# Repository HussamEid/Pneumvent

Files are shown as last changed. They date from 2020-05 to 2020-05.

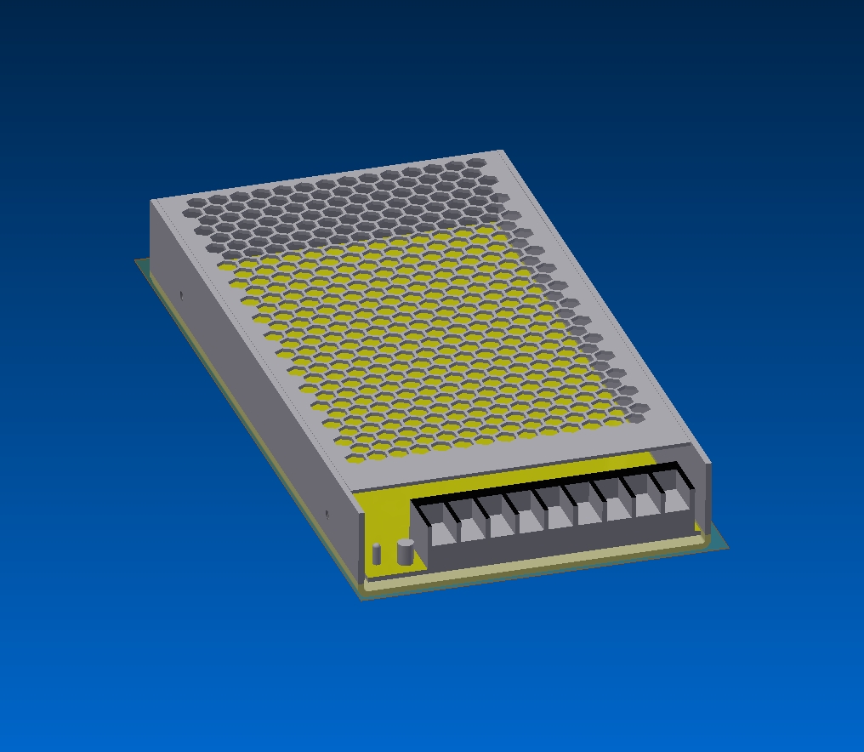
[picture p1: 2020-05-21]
Assembly/LRS-200/Fuente meanwell LRS-200-12.jpg

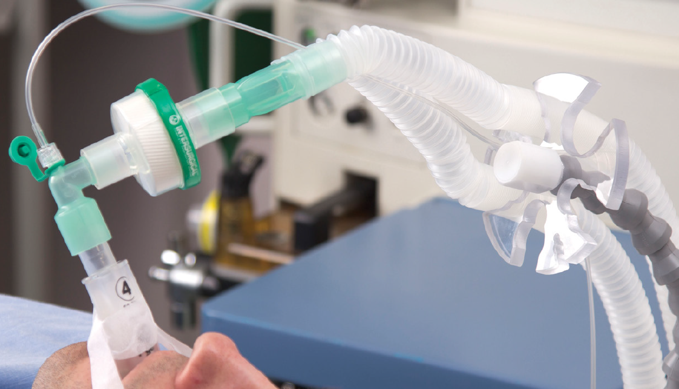
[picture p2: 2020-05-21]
Assembly/Tubing/Overview.PNG

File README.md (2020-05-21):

# Pneumvent
  An open source ICU grade ventilator with feedback control, various operation modes and an easy to use UI. This ventilator was created in response to the COVID-19 pandemic and help address the shortages of the ventilators world wide.
=======
  An open source ICU grade ventilator with feedback control, various operation modes and an easy to use UI. This ventilator was created in response to the COVID-19 pandemic and help address the shortages of the ventilators world wide.
T
>>>>>>> 2d3a161cecc6a0071c0be55cc0cbad3aadb7b60b

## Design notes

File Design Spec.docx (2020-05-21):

# Block Diagram

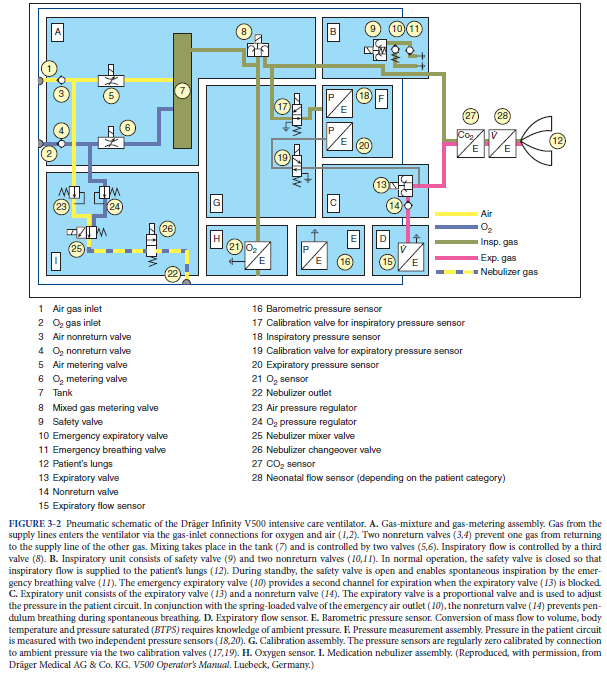
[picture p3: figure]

P.67 (Martin)

# Power Input

INPUT: 110/240VAC @ 50/60Hz,

Battery: 10 – 30VDC

Outlet Pressure (o2/Air): 50psi

Internal Pressure regulator: ~20psi

# Air Conditioning:

Warmed air

Humidified Air

# Mechanism:

Air Compressor or Air blower

# Design Spec

## Battery

The battery requirements are as follows:

12V, at least, 60Ah , lead-acid for reduced cost. This would mean that the system is capable of running at least for 190 mins at full load (worst case scenario).

The battery is connected to the circuit via a screw terminal. The circuit is protected from accidental reverse polarity connection of the battery as well as battery transients due to load variation.

## Power Supply

A three terminal IEC complaint medical grade power entry receptable is used to power the system in case the battery is not used or can be used to charge the battery and power the system if the battery is hooked up the system.

The device can accept voltage inputs ranging from 85VAC to 250VAC and thus can be used around the globe without concern to the outlet voltage.

The system is also fused incase of failure both due to internal and/or external factors. Once the wall power enters the system the whole unit is powered using an Isolated 12V. This means that all users and patients are completely isolated from the mains power supply aacccording ISO 80601.

# Processor

There are multiple sensors (instrumentation) and transducers being monitored and regulated as such a high performance MCU was chosen , in this case STM32F40LVCT6. The MCU will be responsible for :

- Assisting, monitoring and controlling of ventilation
- Control air mixture percentage
- A Human interface beduim to allow the opreator to monitor and control main parameters such as repiratino pressure provide feedback to the users such as control mode and measured snensor data
- Use PID control system algorithm to function 4 valves

The reason this processor was chosen was due to the following:

- High efficency with low voltage (3.3V)
- 32-bit ARM cortex –M4
- 246KB flash memory/512bytes OTP memory /64KB SRAM
- BOR monitoring
- 16 channel ADC (12-bit)
- 11 timers
- 3x I2C interfances
- Accurate measurements and fast control

# Alarm system

Using measured patient data such as exhaled volume and airway pressure, the ventilation system will be able to detect whether a breath has been taken. If the controller detects that no inhalation takes place within a certain period of time the controller will sound a buzzer at 4KHz and 90dB. There are different beeping sequence for different conditions which will be controlled by the MCU.

Also a bright red LED will be flashing to indicate a fault condition.

## Actuators

There are 4 electromechanical valves that are used as following:

- Control O2 input
- Control Air compressor input
- Manage Inhaled air pressure
- Manage Exhaled air pressure

. Each of those valves operate at 5V. Due to the large inductances associated with switching the valves the 5V is galvanically isolated from the MCU and is controlled using optocouplers.

## Pressure Sensors

There are 4 pressure sensors that are used as analog sensor inputs to the MCU to regulate air flow, namey:

1- 1x Lung Pressure Sensor- It is used to calculated the volume of air in the lungs via the pneumotachometer tubing
2- 1x Tank Pressure Sensor- It is used to determine the air to oxygen mixture ratio
3- 2x Differential Pressure Sensor (Flow sensor) used to determine the volume of air inhaled and volume of air exhaled respectively

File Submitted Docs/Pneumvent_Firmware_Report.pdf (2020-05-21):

## Firmware Project Configuration Report

# 1. Description

## 1.1. MCU

MCU Series | STM32F4
MCU Line | STM32F401
MCU name | STM32F401VCTx
MCU Package | LQFP100
MCU Pin number | 100

# PNEUMVENT FIRMWARE REPORT

Agorize- Code Life Ventilator | Hussam Eid | info@hussameid.com

# 2. Pinout Configuration

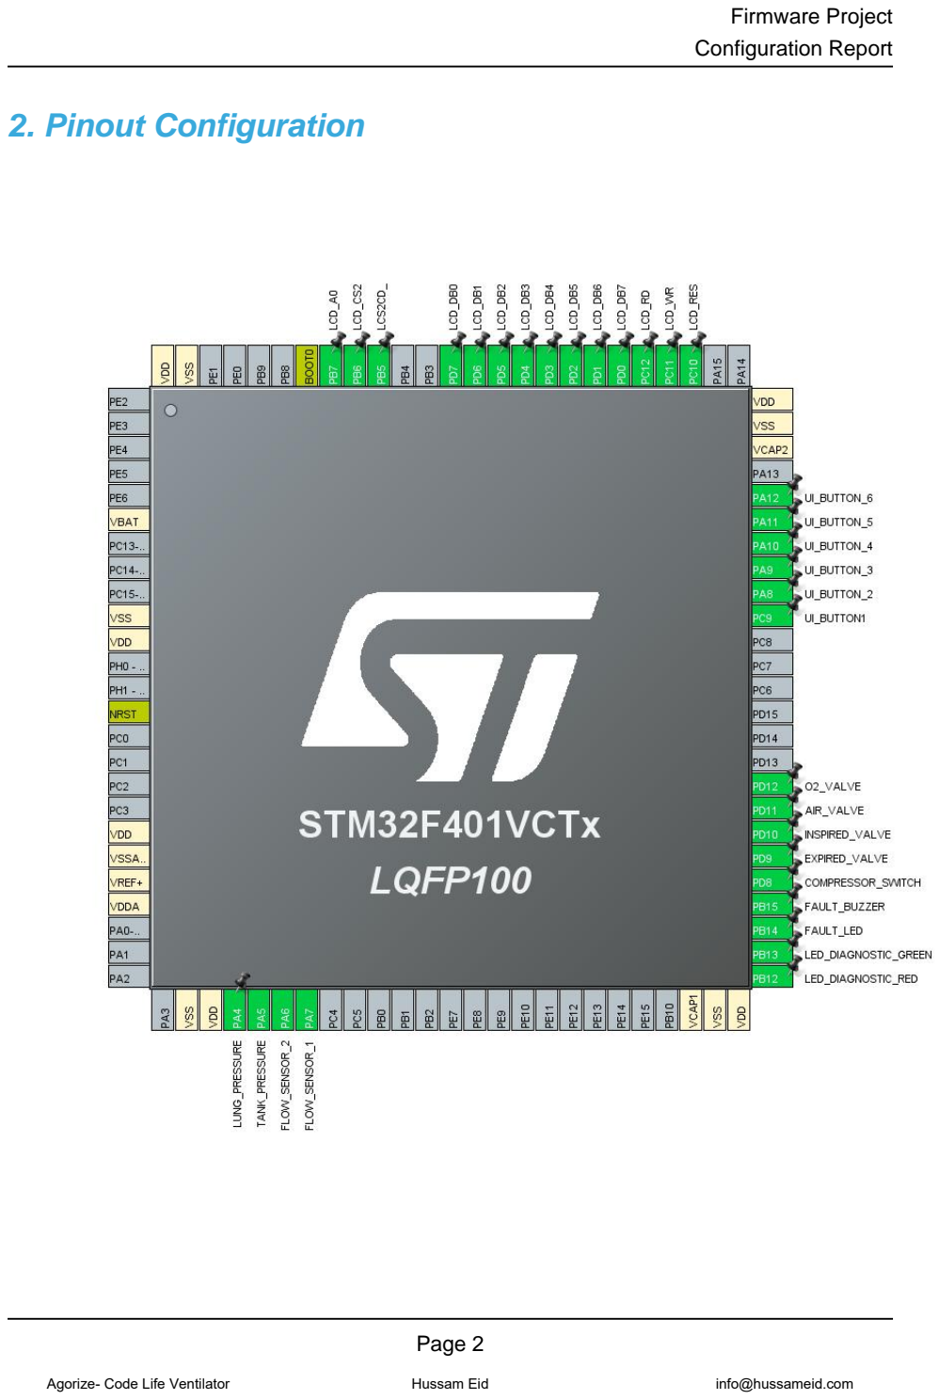
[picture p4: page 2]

# 3. Pins Configuration

Pin Number LQFP100 | Pin Name (function after reset) | Pin Type | Alternate Function(s) | Label
6 | VBAT | Power
10 | VSS | Power
11 | VDD | Power
14 | NRST | Reset
19 | VDD | Power
20 | VSSA/VREF- | Power
21 | VREF+ | Power
22 | VDDA | Power
27 | VSS | Power
28 | VDD | Power
29 | PA4 | I/O | ADC1_IN4 | LUNG_PRESSURE
30 | PA5 | I/O | ADC1_IN5 | TANK_PRESSURE
31 | PA6 | I/O | ADC1_IN6 | FLOW_SENSOR_2
32 | PA7 | I/O | ADC1_IN7 | FLOW_SENSOR_1
48 | VCAP1 | Power
49 | VSS | Power
50 | VDD | Power
51 | PB12 * | I/O | GPIO_Output | LED_DIAGNOSTIC_RED
52 | PB13 * | I/O | GPIO_Output | LED_DIAGNOSTIC_GREE N
53 | PB14 * | I/O | GPIO_Output | FAULT_LED
54 | PB15 * | I/O | GPIO_Output | FAULT_BUZZER
55 | PD8 * | I/O | GPIO_Output | COMPRESSOR_SWITCH
56 | PD9 * | I/O | GPIO_Output | EXPIRED_VALVE
57 | PD10 * | I/O | GPIO_Output | INSPIRED_VALVE
58 | PD11 * | I/O | GPIO_Output | AIR_VALVE
59 | PD12 * | I/O | GPIO_Output | O2_VALVE
66 | PC9 * | I/O | GPIO_Input | UI_BUTTON1
67 | PA8 * | I/O | GPIO_Input | UI_BUTTON_2
68 | PA9 * | I/O | GPIO_Input | UI_BUTTON_3
69 | PA10 * | I/O | GPIO_Input | UI_BUTTON_4
70 | PA11 * | I/O | GPIO_Input | UI_BUTTON_5
71 | PA12 * | I/O | GPIO_Input | UI_BUTTON_6
73 | VCAP2 | Power
74 | VSS | Power
75 | VDD | Power

Pin Number LQFP100 | Pin Name (function after reset) | Pin Type | Alternate Function(s) | Label
78 | PC10 * | I/O | GPIO_Output | LCD_RES
79 | PC11 * | I/O | GPIO_Output | LCD_WR
80 | PC12 * | I/O | GPIO_Output | LCD_RD
81 | PD0 * | I/O | GPIO_Output | LCD_DB7
82 | PD1 * | I/O | GPIO_Output | LCD_DB6
83 | PD2 * | I/O | GPIO_Output | LCD_DB5
84 | PD3 * | I/O | GPIO_Output | LCD_DB4
85 | PD4 * | I/O | GPIO_Output | LCD_DB3
86 | PD5 * | I/O | GPIO_Output | LCD_DB2
87 | PD6 * | I/O | GPIO_Output | LCD_DB1
88 | PD7 * | I/O | GPIO_Output | LCD_DB0
91 | PB5 * | I/O | GPIO_Output | LCS2CD_
92 | PB6 * | I/O | GPIO_Output | LCD_CS2
93 | PB7 * | I/O | GPIO_Output | LCD_A0
94 | BOOT0 | Boot
99 | VSS | Power
100 | VDD | Power

## * The pin is affected with an I/O function

# 4. Clock Tree Configuration

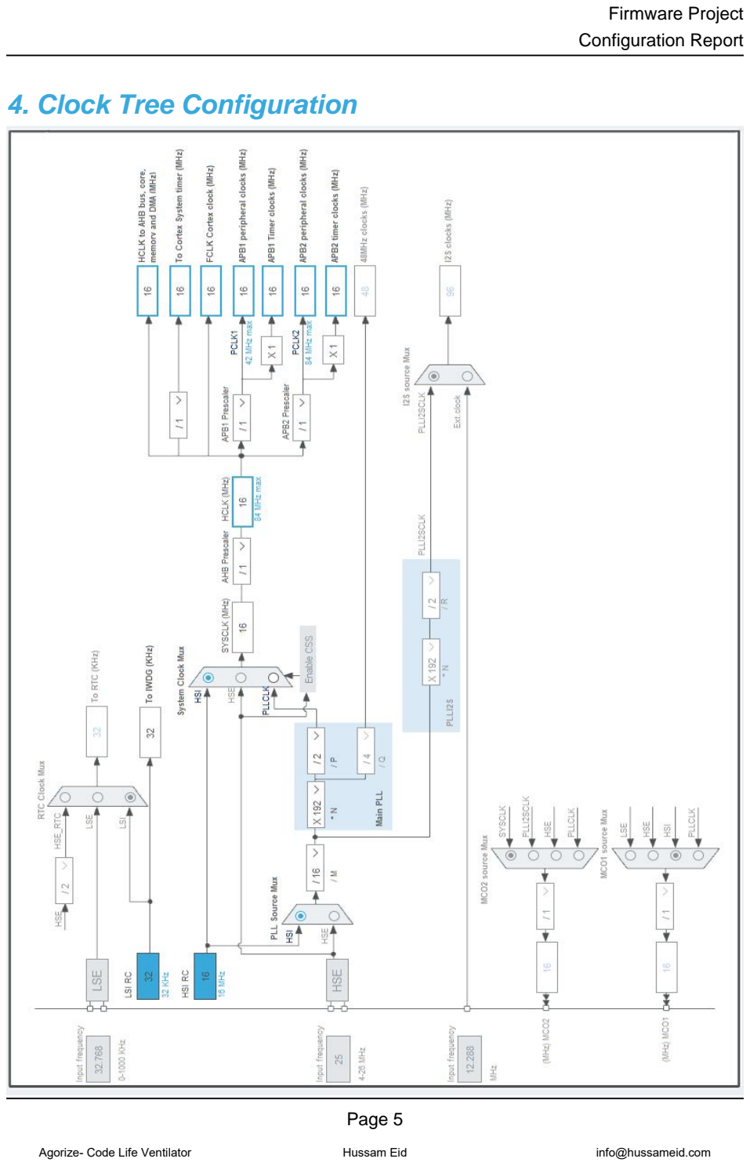
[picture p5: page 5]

# 5. Software Project

## 5.1. Project Settings

# 6. Power Consumption Calculator report

### 6.1. Microcontroller Selection

Series | STM32F4
Line | STM32F401
MCU | STM32F401VCTx
Datasheet | 024738_Rev8

### 6.2. Parameter Selection

Temperature | 25
Vdd | 3.3

### 6.3. Battery Selection

## Battery Capacity Self Discharge

Nominal Voltage | 3.6 V
Max Cont Current | 100.0 mA
Max Pulse Current | 200.0 mA
Cells in series | 1
Cells in parallel | 1

## 6.4. Sequence

Step | Step1 | Step2
Mode | RUN | STOP
Vdd | 3.3 | 3.3
Voltage Source | Battery | Battery
Range | Scale2-Medium | No Scale
Fetch Type | FLASH/ART/PREFETCH | n/a
CPU Frequency | 84 MHz | 0 Hz
Clock Configuration | HSE PLL | Regulator_LPLV Flash-PwrDwn
Clock Source Frequency | 4 MHz | 0 Hz

### Peripherals

Additional Cons. | 0 mA | 0 mA
Average Current | 21.2 mA | 10 µA
Duration | 0.1 ms | 0.9 ms
DMIPS | 105.0 | 0.0
Ta Max | 102.06 | 105
Category | In DS Table | In DS Table

## 6.5. RESULTS

Sequence Time | 1 ms | Average Current | 2.13 mA
Battery Life | 2 months, 5 days, 14 hours | Average DMIPS | 105.0 DMIPS

## 6.6. Chart

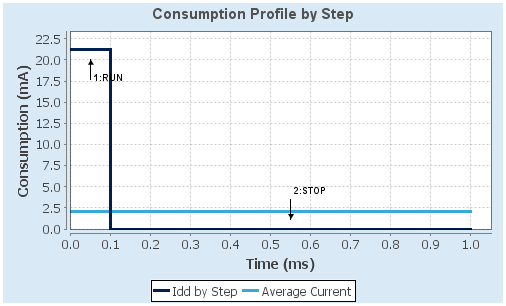
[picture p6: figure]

# 7. IPs and Middleware Configuration

# 7.1. ADC1

## mode: IN4 mode: IN5 mode: IN6 mode: IN7 mode: Temperature Sensor Channel 7.1.1. Parameter Settings:

### ADC_Settings:

Clock Prescaler | PCLK2 divided by 2
Resolution | 12 bits (15 ADC Clock cycles)
Data Alignment | Right alignment
Scan Conversion Mode | Disabled
Continuous Conversion Mode | Enabled *
Discontinuous Conversion Mode | Disabled
DMA Continuous Requests | Disabled
End Of Conversion Selection | EOC flag at the end of single channel conversion

### ADC_Regular_ConversionMode:

Number Of Conversion | 1
External Trigger Conversion Source | Regular Conversion launched by software
External Trigger Conversion Edge | None
Rank | 1
Channel | Channel 4
Sampling Time | 3 Cycles

### ADC_Injected_ConversionMode:

Number Of Conversions | 0

### WatchDog:

Enable Analog WatchDog Mode | false

# 7.2. GPIO

# 7.3. IWDG

## mode: Activated 7.3.1. Parameter Settings:

### Clocking:

IWDG counter clock prescaler | 4
IWDG down-counter reload value | 4095

# 7.4. RCC

## 7.4.1. Parameter Settings:

### System Parameters:

VDD voltage (V) | 3.3
Instruction Cache | Enabled
Prefetch Buffer | Enabled
Data Cache | Enabled
Flash Latency(WS) | 0 WS (1 CPU cycle)

### RCC Parameters:

HSI Calibration Value | 16
TIM Prescaler Selection | Disabled
HSE Startup Timout Value (ms) | 100
LSE Startup Timout Value (ms) | 5000

### Power Parameters:

Power Regulator Voltage Scale | Power Regulator Voltage Scale 2

# 7.5. SYS

## Timebase Source: SysTick

# 7.6. TIM3

## Clock Source : Internal Clock 7.6.1. Parameter Settings:

### Counter Settings:

Prescaler (PSC - 16 bits value) | 0
Counter Mode | Up
Counter Period (AutoReload Register - 16 bits value ) | 0
Internal Clock Division (CKD) | No Division
auto-reload preload | Disable

### Trigger Output (TRGO) Parameters:

Master/Slave Mode (MSM bit) | Disable (Trigger input effect not delayed)
Trigger Event Selection | Reset (UG bit from TIMx_EGR)

# 7.7. WWDG

## mode: Activated 7.7.1. Parameter Settings:

### Watchdog Clocking:

WWDG counter clock prescaler | 1
WWDG window value | 64
WWDG free-running downcounter value | 64

### Watchdog Interrupt:

Early wakeup interrupt | Disable

### * User modified value

# 8. System Configuration

# 8.1. GPIO configuration

IP | Pin | Signal | GPIO mode | GPIO pull/up pull down | Max Speed | User Label
ADC1 | PA4 | ADC1_IN4 | Analog mode | No pull-up and no pull-down | n/a | LUNG_PRESSURE
| PA5 | ADC1_IN5 | Analog mode | No pull-up and no pull-down | n/a | TANK_PRESSURE
| PA6 | ADC1_IN6 | Analog mode | No pull-up and no pull-down | n/a | FLOW_SENSOR_2
| PA7 | ADC1_IN7 | Analog mode | No pull-up and no pull-down | n/a | FLOW_SENSOR_1
GPIO | PB12 | GPIO_Output | Output Push Pull | No pull-up and no pull-down | Low | LED_DIAGNOSTIC_RED
PB13 | GPIO_Output | Output Push Pull | No pull-up and no pull-down | Low | LED_DIAGNOSTIC_GREE N
PB14 | GPIO_Output | Output Push Pull | No pull-up and no pull-down | Low | FAULT_LED
PB15 | GPIO_Output | Output Push Pull | No pull-up and no pull-down | Low | FAULT_BUZZER
PD8 | GPIO_Output | Output Push Pull | No pull-up and no pull-down | Low | COMPRESSOR_SWITCH
PD9 | GPIO_Output | Output Push Pull | No pull-up and no pull-down | Low | EXPIRED_VALVE
PD10 | GPIO_Output | Output Push Pull | No pull-up and no pull-down | Low | INSPIRED_VALVE
PD11 | GPIO_Output | Output Push Pull | No pull-up and no pull-down | Low | AIR_VALVE
PD12 | GPIO_Output | Output Push Pull | No pull-up and no pull-down | Low | O2_VALVE
PC9 | GPIO_Input | Input mode | No pull-up and no pull-down | n/a | UI_BUTTON1
PA8 | GPIO_Input | Input mode | No pull-up and no pull-down | n/a | UI_BUTTON_2
PA9 | GPIO_Input | Input mode | No pull-up and no pull-down | n/a | UI_BUTTON_3
PA10 | GPIO_Input | Input mode | No pull-up and no pull-down | n/a | UI_BUTTON_4
PA11 | GPIO_Input | Input mode | No pull-up and no pull-down | n/a | UI_BUTTON_5
PA12 | GPIO_Input | Input mode | No pull-up and no pull-down | n/a | UI_BUTTON_6
PC10 | GPIO_Output | Output Push Pull | No pull-up and no pull-down | Low | LCD_RES
PC11 | GPIO_Output | Output Push Pull | No pull-up and no pull-down | Low | LCD_WR
PC12 | GPIO_Output | Output Push Pull | No pull-up and no pull-down | Low | LCD_RD
PD0 | GPIO_Output | Output Push Pull | No pull-up and no pull-down | Low | LCD_DB7
PD1 | GPIO_Output | Output Push Pull | No pull-up and no pull-down | Low | LCD_DB6
PD2 | GPIO_Output | Output Push Pull | No pull-up and no pull-down | Low | LCD_DB5
PD3 | GPIO_Output | Output Push Pull | No pull-up and no pull-down | Low | LCD_DB4
PD4 | GPIO_Output | Output Push Pull | No pull-up and no pull-down | Low | LCD_DB3
PD5 | GPIO_Output | Output Push Pull | No pull-up and no pull-down | Low | LCD_DB2
PD6 | GPIO_Output | Output Push Pull | No pull-up and no pull-down | Low | LCD_DB1
PD7 | GPIO_Output | Output Push Pull | No pull-up and no pull-down | Low | LCD_DB0
PB5 | GPIO_Output | Output Push Pull | No pull-up and no pull-down | Low | LCS2CD_
PB6 | GPIO_Output | Output Push Pull | No pull-up and no pull-down | Low | LCD_CS2
PB7 | GPIO_Output | Output Push Pull | No pull-up and no pull-down | Low | LCD_A0

# 8.2. DMA configuration

## nothing configured in DMA service

# 8.3. NVIC configuration

Interrupt Table | Enable | Preenmption Priority | SubPriority
Non maskable interrupt | true | 0 | 0
Hard fault interrupt | true | 0 | 0
Memory management fault | true | 0 | 0
Pre-fetch fault, memory access fault | true | 0 | 0
Undefined instruction or illegal state | true | 0 | 0
System service call via SWI instruction | true | 0 | 0
Debug monitor | true | 0 | 0
Pendable request for system service | true | 0 | 0
System tick timer | true | 0 | 0
ADC1 global interrupt | true | 0 | 0
Window watchdog interrupt | unused
PVD interrupt through EXTI line 16 | unused
Flash global interrupt | unused
RCC global interrupt | unused
TIM3 global interrupt | unused
FPU global interrupt | unused

### * User modified value

# 9. Predefined Views - Category view : Current

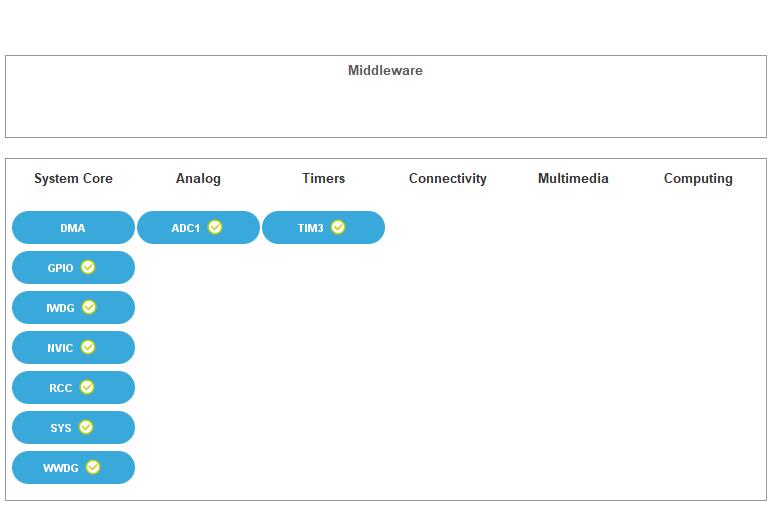
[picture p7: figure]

# 10. Software Pack Report

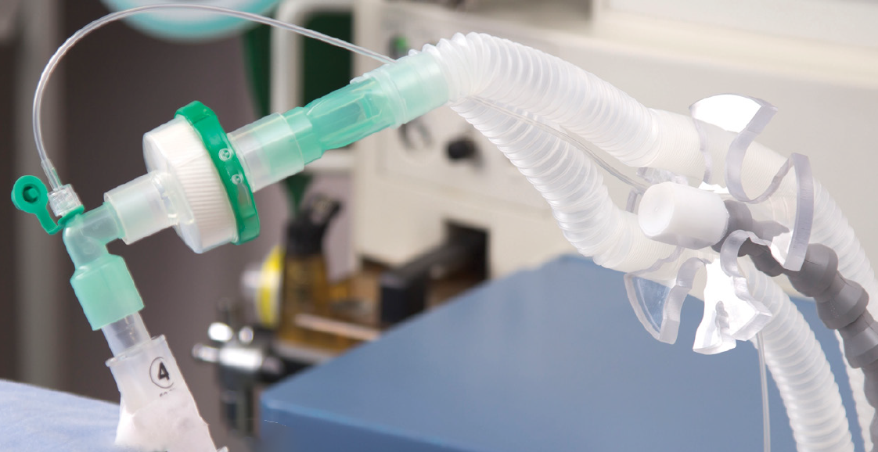
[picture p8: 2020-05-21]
Assembly/Tubing/Overview2.png

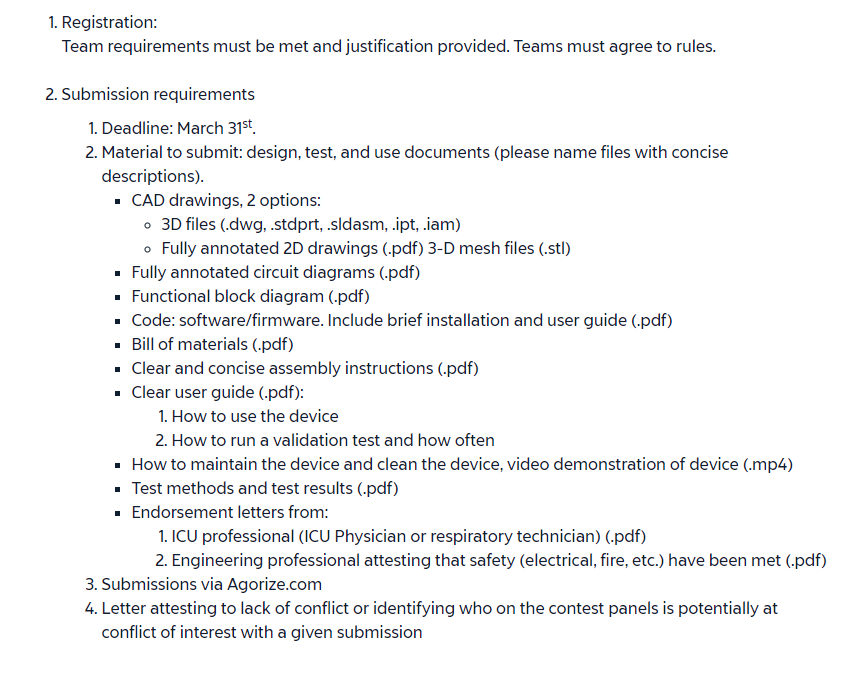
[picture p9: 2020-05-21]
Submission Req.PNG

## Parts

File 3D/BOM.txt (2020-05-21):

3DX_CUI_DEVICES_Supplier: CUI Devices
3DX_CUI_DEVICES_Description: 16.5 mm, 12 Vp-p, 85 dB, Through Hole, Piezo Audio Transducer Buzzer
3DX_CUI_DEVICES_Model Number: CPT-1667-85T

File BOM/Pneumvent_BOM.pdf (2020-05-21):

Item No. | Description | Manufacturer | Manufacturer Part Number | Designator | Quantity
1 | 15A 60PSI Compressor | McMaster | 4251K71 | M2 | 1
2 | 2/2 Air solenoid valve | Festo | MHP1-M4H-2/2G-M3-TC | M11, M12 | 2
3 | 2/2 Air solenoid valve | Festo | MHP1-M4H-3/2GM3-TC | M23, M24 | 2
4 | 2/2 Electrovalves Plate | Festo | MHP1-AS-2-M3 | M5, M6 | 2
5 | 2/2 Electrovalves Plate | Festo | MHP1-AS-3-M3 | M17, M18 | 2
6 | 22mm Compact, extendable breathing system with luer elbow, 1.5m | Intersurgical | 2150000 | M34 | 1
7 | 3.9µH Shielded Wirewound Inductor 4.2A 26.4mOhm Max Nonstandard | Murata | 1255AY-3R9N=P3 | L1 | 1
8 | 4mm Plastic Tubing | Festo | PUN-H-4X0,75-BL | M30 | 1
9 | ARM® Cortex®-M4 STM32F4 Microcontroller IC 32-Bit 84MHz 256KB (256K x 8) FLASH 100-LQFP (14x14) | STMicroelectronics | STM32F401VCT6 | IC1 | 1
10 | Battery 12V 75Ah | Powersonic | PS-12750S | M33 | 1
11 | BI-DIRECTIONAL ESD PROTECTION DI | Toshiba Semiconductor and Storage | DF2B26M4SL,L3F | D2 | 1
12 | BUZZER, 16.5 MM, 6.7 MM DEEP, P, | CUI | CPT-1667-85T | B1 | 1
13 | CAP 6.8 UF 20% 50 V | Wurth Electronics | 865080642005 | C29, C31, C35, C37, C41 | 5
14 | CAP ALUM 47UF 20% 50V SMD | Panasonic | EEE-1HA470XAP | C2 | 1
15 | CAP CER 0.1UF 50V X7R 0603 | KEMET | C0603C104M5RACTU | C1, C6, C7, C8, C9, C10, C12, C13, C14, C15, C16, C18, C19, C20, C21, C24, C25, C39, C43, C44, C45, C46, C47, C48, C49, C50, C51, C52, C53, C54, C55, C56, C57, C58, C59, C60 | 36
16 | CAP CER 0.33UF 50V X5R 0603 | TDK | C1608X5R1H334K080AB | C17 | 1
17 | CAP CER 10UF 25V X7R 1206 | Samsung | CL31A106MBHNNNE | C3 | 1
18 | CAP CER 1nF 50V X7R 0603 | KEMET | C0603C104M5RACTU | C30, C33, C36, C38, C42 | 5
19 | CAP CER 1UF 16V X7R 0603 | KEMET | C0603C104M5RACTU | C26 | 1
20 | CAP CER 2.2nF 50V X7R 0603 | KEMET | C0603C104M5RACTU | C27, C28, C32, C34, C40 | 5
21 | CAP CER 2.2UF 16V X5R 0603 | KEMET | C0603C225K4PACTU | C11, C23 | 2
22 | CAP CER 22UF 10V X5R 0805 | Taiyo Yuden | LMK212BBJ226MG-T | C4, C5 | 2
23 | CAP CER 4.7UF 10V X5R 0603 | Taiyo Yuden | LMK107BJ475KA-T | C22 | 1
24 | Clamp Ipp Tvs Diode Surface Mount SOT-323-5 | STMicroelectronics | ESDALC6V1W5 | IC2 | 1

# PNEUMVENT BOM

Item No. | Description | Manufacturer | Manufacturer Part Number | Designator | Quantity
25 | CONN RCPT 20POS 0.05 GOLD PCB | Amphenol ICC (FCI) | 20021311-00020T4LF | M31 | 1
26 | CORD 18AWG 5-15P - 320-C13 9.84' | Assmann WSW Components | A-PC2302-030021-1 | M32 | 1
27 | DC DC CONVERTER 5V 1W | Recom | RFB-0505S | PS2, PS3, PS4, PS5, PS6 | 5
28 | DIODE SCHOTTKY 200V 5A SMC | SMC | SK520TR | D1, D4, D5, D6 | 4
29 | Enclosed AC DC Converters 1 Output 12V 17A 90 ~ 132 VAC, 180 ~ 264 VAC, 240 ~ 370 VDC Input | Mean Well | LRS-200-12 | M1 | 1
30 | FERRITE BEAD 300 OHM 0603 1LN | Vishay Dale | ILBB0603ER301V | L2 | 1
31 | Header, 13-Pin | Sullins | PREC013SAAN-RC | P1 | 1
32 | Header, 6-Pin | Sullins | PRPC006SACN-RC | J3 | 1
33 | HOOK-UP DUAL STRND 20AWG WHT 5' | 81044/12-20-9 | 20 AWG WIRE | M4 | 1
34 | IC INST AMP 1 CIRCUIT 8VSSOP | Texas Instruments | INA826AIDGKR | IC9, IC10 | 2
35 | IC PWR DRVR N-CHAN 1:1 SOT23-3 | ON Semiconductor | NUD3124LT1G | U1 | 1
36 | IC REG BUCK 3.3V 2A TSOT26 | Diodes | AP63203WU-7 | PS1 | 1
37 | Inductor Unshielded Wirewound 190mA 4.81Ohm Max 0805 (2012 Metric) | Taiyo Yuden | CBC2012T220M | L3, L4, L5, L6, L7 | 5
38 | LCD MOD GRAPH 122X32 WH TRANSM | Newhaven Display | NHD-12232KZ-NSW-BBW-P | IC11 | 1
39 | LED GREEN CLEAR 0603 SMD | Wurth Electronics | 150060RS75000 | LED3 | 1
40 | LED GREEN CLEAR 0603 SMD | Wurth Electronics | 150060VS75000 | LED1, LED2 | 2
41 | Linear Voltage Regulator IC 1 Output 100mA 8-SOIC | Texas Instruments | UA78L12ACD | IC4 | 1
42 | MEMS OSC XO 2.0000KHZ CMOS SMD | Microchip | DSC6083HI2A-002K000T | Y1 | 1
43 | MOSFET N-CH 60V 300MA SOT-23 | Rohm | RYE002N05TCL | Q1, Q2 | 2
44 | OPTOISOLTR 5KV 4CH TRANS 16-SMD | Vishay Lite-On | LTV-847S | IC3 | 1
45 | Plug socket with cable for Valves | Festo | KMH-0,5 | M25, M26, M27, M28 | 4
46 | Power Entry Connector Receptacle, Male Blades IEC 320-C14 Panel Mount, Flange | Schaffner | FN9222B-1-06 | M3 | 1
47 | PRESSURE SENSOR DUAL PORT 8SOP | NXP USA Inc. | MPXV7002DPT1 | IC5, IC6 | 2
48 | Push-in fitting | Festo | QSM-M3-4-I | M13, M14, M15, M16, M19, M20, M21, M22 | 8
49 | Push-in fitting 1/4mm to 4mm | Festo | QS-1/4-4 | M7, M8, M9, M10 | 4
50 | Push-in Y-connector | Festo | QSY-8-4 | M29 | 1
51 | Red 620nm LED Indication -Discrete 2.4V 1113 (2835 Metric) | QT-Brightek | QBHP686-RH | LED4 | 1

Item No. | Description | Manufacturer | Manufacturer Part Number | Designator | Quantity
52 | RELAY AUTOMOTIVE SPST 15A 12V | Panasonic | JSM1A-12V-5 | RE2 | 1
53 | RELAY GEN PURPOSE SPDT 20A 12V | TE Connectivity P&B | T9GV5L14-12 | RE1 | 1
54 | RES 20 OHM 1% 1/2W 1206 | Stackpole Electronics | RNCP1206FTD20R0 | R14, R15, R16 | 3
55 | RES SMD 0 OHM JUMPER 1/10W 0603 | Panasonic | ERJ-3GEY0R00V | R2, R4, R5, R7, R27 | 5
56 | RES SMD 1.2K OHM 1% 1/4W 1206 | Yageo | RC1206FR-071K2L | R17 | 1
57 | RES SMD 100K OHM 0.5% 1/16W 0603 | Susumu | RR0816P-104-D | R28, R30 | 2
58 | RES SMD 10K OHM 1% 1/4W 1206 | Yageo | RC1206FR-07200RL | R1, R11, R12, R13, R18, R19, R20, R21, R22, R23, R24, R25, R44, R45, R46, R47, R48, R49, R50 | 19
59 | RES SMD 10K OHM 5% 1/10W 0603 | Yageo | RC0603JR-0710KL | R3, R8, R9, R10, R26 | 5
60 | RES SMD 200K OHM 0.5% 1/16W 0603 | Susumu | RR0816P-204-D | R29, R31 | 2
61 | RES SMD 6K04 OHM 0.5% 1/16W 0603 | Stackpole Electronics | RMCF0603FT6K04 | R33, R39 | 2
62 | RES SMD100K OHM 0.5% 1/16W 0603 | Susumu | RR0816P-104-D | R32, R34, R35, R36, R37, R38, R40, R41, R42, R43 | 10
63 | RESISTOR 47 Ohms ±5% 0.1W, 1/10W Chip Resistor 0603 | TE Connectivity | CRGCQ0603J47R | R6 | 1
64 | Screws for WH/WQ Series Enclosures | PolyCase | SCREWS-007-50 | M37 | 1
65 | SENS PRESSURE 7.25 PSI MAX MPAK | NXP Freescale | MPXM2053GST1 | IC7 | 1
66 | SENSOR GAUGE PRESS 14.5PSI MAX | NXP Freescale | MPXV2102GP | IC8 | 1
67 | SWITCH TACT SPST-NO 0.025A 50V | E-Switch | 320E11BLK | SW2, SW3, SW4, SW5, SW6, SW7 | 6
68 | Tactile Switch SPST-NO Top Actuated Surface Mount | ITT C&K | PTS526SM15SMTR2LFS | SW1 | 1
69 | TERM BLK 2POS SIDE ENTRY 5MM PCB | Phoenix Contact | 1935161 | J1, J2, J4, J9, J10, J11, J12 | 7
70 | Test Point | N/A | N/A | TP1, TP2, TP3, TP4, TP5, TP6, TP7, TP8, TP9, TP10, TP11 | 11
71 | TVS Diode (Uni-directional) | STMicroelectronics | ESDALC6V1-1U2 | D3 | 1
72 | Vixen Air Inflation Schrader Valve with Push to Connect (PTC) for 1/4" OD Air Line | Vixen Air Inflation | VXA1014-2 | M35 | 1
73 | WQ-64 NEMA Hinged Enclosure 0.43 x 0.31 x 0.31 in | PolyCase | WQ-64 | M36 | 1

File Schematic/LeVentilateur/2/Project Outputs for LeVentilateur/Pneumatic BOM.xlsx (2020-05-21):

Description | Designator | Manufacturer Part Number 1 | Quantity | Comment | Manufacturer 1
2/2 Electrovalves Plate | M5, M6 | MHP1-AS-2-M3 | 2 | 2/2 Electrovalves Plate | Festo
Push-in fitting 1/4mm to 4mm | M7, M8, M9, M10 | QS-1/4-4 | 4 | Reduction Fitting | Festo
2/2 Air solenoid valve | M11, M12 | MHP1-M4H-2/2G-M3-TC | 2 | 2/2 Air solenoid valve | Festo
Push-in fitting | M13, M14, M15, M16, M19, M20, M21, M22 | QSM-M3-4-I | 8 | Push-in fitting | Festo
2/2 Electrovalves Plate | M17, M18 | MHP1-AS-3-M3 | 2 | 3/2 Electrovalves Plate | Festo
2/2 Air solenoid valve | M23, M24 | MHP1-M4H-3/2GM3-TC | 2 | 3/2 Air solenoid valve | Festo
Plug socket with cable for Valves | M25, M26, M27, M28 | KMH-0,5 | 4 | Plug socket with cable | Festo
Push-in Y-connector | M29 | QSY-8-4 | 1 | Push-in Y-connector | Festo
4mm Plastic Tubing | M30 | PUN-H-4X0,75-BL | 1 | Tubing 4mm | Festo

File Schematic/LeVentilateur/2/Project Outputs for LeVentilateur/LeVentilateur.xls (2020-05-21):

Description | Designator | Manufacturer Part Number 1 | Quantity | Comment | Manufacturer 1
Header, 6-Pin | J3 | PRPC006SACN-RC | 1 | Header 6 | Sullins
Test Point | TP1, TP2, TP3, TP4, TP5, TP6, TP7, TP8, TP9, TP10, TP11, TP12 |  | 12 | TP | N/A, [NoParam]
HOOK-UP DUAL STRND 20AWG WHT 5' | M4 | 20 AWG WIRE | 1 | 15 AWG WIRE | 81044/12-20-9
CONN RCPT 20POS 0.05 GOLD PCB | M31 | 20021311-00020T4LF | 1 | 20 POS FEMALE Receptacle Connector | Amphenol ICC (FCI)
CORD 18AWG 5-15P - 320-C13 9.84' | M32 | A-PC2302-030021-1 | 1 | POWER CORD 18AWG NORTH AMERICAN | Assmann WSW Components
Power Entry Connector Receptacle, Male Blades IEC 320-C14 Panel Mount, Flange | M3 | FN9222B-1-06 | 1 | Power Entry Receptacle | Schaffner
RELAY AUTOMOTIVE SPST 15A 12V | RE2 | JSM1A-12V-5 | 1 | RELAY-SPST | Panasonic
Plug socket with cable for Valves | M25, M26, M27, M28 | KMH-0,5 | 4 | Plug socket with cable | Festo
Enclosed AC DC Converters 1 Output 12V 17A 90 ~ 132 VAC, 180 ~ 264 VAC, 240 ~ 370 VDC Input | M1 | LRS-200-12 | 1 | 12V 204W PS | Mean Well
2/2 Electrovalves Plate | M5, M6 | MHP1-AS-2-M3 | 2 | 2/2 Electrovalves Plate | Festo
2/2 Electrovalves Plate | M17, M18 | MHP1-AS-3-M3 | 2 | 3/2 Electrovalves Plate | Festo
2/2 Air solenoid valve | M11, M12 | MHP1-M4H-2/2G-M3-TC | 2 | 2/2 Air solenoid valve | Festo
2/2 Air solenoid valve | M23, M24 | MHP1-M4H-3/2GM3-TC | 2 | 3/2 Air solenoid valve | Festo
Header, 13-Pin | P1 | PREC013SAAN-RC | 1 | Header 13 | Sullins
4mm Plastic Tubing | M30 | PUN-H-4X0,75-BL | 1 | Tubing 4mm | Festo
Push-in fitting 1/4mm to 4mm | M7, M8, M9, M10 | QS-1/4-4 | 4 | Reduction Fitting | Festo
Push-in fitting | M13, M14, M15, M16, M19, M20, M21, M22 | QSM-M3-4-I | 8 | Push-in fitting | Festo
Push-in Y-connector | M29 | QSY-8-4 | 1 | Push-in Y-connector | Festo
CONN HDR 20POS 0.05 GOLD SMD | M38 | SFH31-NPPB-D10-SP-BK | 1 | LCD Connector | Sullins Connector Solutions
RELAY GEN PURPOSE SPDT 20A 12V | RE1 | T9GV5L14-12 | 1 | RELAY-SPDT | TE Connectivity P&B
3.9µH Shielded Wirewound Inductor 4.2A 26.4mOhm Max Nonstandard | L1 | 1255AY-3R9N=P3 | 1 | 3.9uH | Murata
22mm Compact, extendable breathing system with luer elbow, 1.5m | M34 | 2150000 | 1 | Spirometer Kit | Intersurgical
15A 60PSI Compressor | M2 | 4251K71 | 1 | Compressor | McMaster
IC REG BUCK 3.3V 2A TSOT26 | PS1 | AP63203WU-7 | 1 | AP63203WU-7 | Diodes
MEMS OSC XO 2.0000KHZ CMOS SMD | Y1 | DSC6083HI2A-002K000T | 1 | 2KHZ | Microchip
IC PWR DRVR N-CHAN 1:1 SOT23-3 | U1 | NUD3124LT1G | 1 | NUD3124LT1G | ON Semiconductor
Battery 12V 75Ah | M33 | PS-12750S | 1 | 12V 75Ah Battery | Powersonic
MOSFET N-CH 60V 300MA SOT-23 | Q1, Q2 | RYE002N05TCL | 2 | ="Part Number" | Rohm
PCB Screws for WH/WQ Series Enclosures 0.43 x 0.31 x 0.31 in | M37 | SCREWS-007-50 | 1 | Screws | PolyCase
Vixen Air Inflation Schrader Valve with Push to Connect (PTC) for 1/4" OD Air Line | M35 | VXA1014-2 | 1 | PTC 1/4" | Vixen Air Inflation
WQ-64 NEMA Hinged Enclosure 14.96 x 11.02 x 5.12 in | M36 | WQ-64 | 1 | Hinged Enclosure | PolyCase
BUZZER, 16.5 MM, 6.7 MM DEEP, P, | B1 | CPT-1667-85T | 1 | Buzzer | CUI
CAP CER 0.1UF 50V X7R 0603 | C1, C6, C7, C8, C9, C10, C12, C13, C14, C15, C16, C18, C19, C20, C21, C24, C25, C29, C39, C43, C44, C45, C46, C47, C48, C49, C50, C51, C52, C53, C54, C55, C56, C57, C58, C59, C60, C61, C62 | C0603C104M5RACTU | 39 | 0.1uF | KEMET
CAP ALUM 47UF 20% 50V SMD | C2 | EEE-1HA470XAP | 1 | 47uF | Panasonic
CAP CER 10UF 25V X7R 1206 | C3 | CL31A106MBHNNNE | 1 | 10uF | Samsung
CAP CER 22UF 10V X5R 0805 | C4, C5 | LMK212BBJ226MG-T | 2 | 22uF | Taiyo Yuden
CAP CER 2.2UF 16V X5R 0603 | C11, C23 | C0603C225K4PACTU | 2 | 2.2uF | KEMET
CAP CER 0.33UF 50V X5R 0603 | C17 | C1608X5R1H334K080AB | 1 | 0.33uF | TDK
CAP CER 4.7UF 10V X5R 0603 | C22 | LMK107BJ475KA-T | 1 | 4.7uF | Taiyo Yuden
CAP CER 1UF 16V X7R 0603 | C26 | C0603C104M5RACTU | 1 | 1uF | KEMET
47uF ±20% 35V SMD,6.3x5.4mm Aluminum Electrolytic Capacitors | C27 | VT1V470M0605 | 1 | 47uF | LCS-ROQANG
Capacitor Polarised 470uF Alum | C28 | CK1C471M-CRF10 | 1 | 470uF | LCS-ST(Semtech)
Capacitor Polarised | C30, C31 | CS1V100M-CRC54 | 2 | 10uF | LCS-ST(Semtech)
Diode | D1 |  | 1 | FERD20H100SB-TR | LCS-STMicroelectronics
TVS Diode (Bi-directional) | D2 | SM6T22CA | 1 | SM6T22CAY | STMicroelectronics
TVS Diode (Uni-directional) | D3 | ESDALC6V1-1U2 | 1 | ESDALC6V1-1U2 | STMicroelectronics
DIODE SCHOTTKY 200V 5A SMC | D4, D5, D6 | SK520TR | 3 | SK520TR | SMC
ARM® Cortex®-M4 STM32F4 Microcontroller IC 32-Bit 84MHz 256KB (256K x 8) FLASH 100-LQFP (14x14) | IC1 |  | 1 | STM32F401VCT6 | STMicroelectronics
Clamp Ipp Tvs Diode Surface Mount SOT-323-5 | IC2 | ESDALC6V1W5 | 1 | ESDALC6V1W5 | STMicroelectronics
OPTOISOLTR 5KV 4CH TRANS 16-SMD | IC3 | LTV-847S | 1 | LTV-847S | Vishay Lite-On
Linear Voltage Regulator IC 1 Output 100mA 8-SOIC | IC4 | UA78L12ACD | 1 | UA78L12ACD | Texas Instruments
IC INST AMP 1 CIRCUIT 8VSSOP | IC5, IC9, IC10 | INA826AIDGKR | 3 | IA | Texas Instruments
SENSOR PRESS DIFF 1PSI | IC6 | NSCDRRN001PDUNV | 1 | DIFF_SENSOR | Honeywell Sensing & Control
SENS PRESSURE 7.25 PSI MAX MPAK | IC7 | MPXM2053GST1 | 1 | 50KPA | NXP Freescale
SENSOR GAUGE PRESS 14.5PSI MAX | IC8 | MPXV2102GP | 1 | 100KPA | NXP Freescale
LCD MOD GRAPH 122X32 WH TRANSM | IC11 | NHD-12232KZ-NSW-BBW-P | 1 | LCD | Newhaven Display
IC REG CHARGE PUMP INV 8SOIC | IC12 | LMC7660IM/NOPB | 1 | LMC7660IM_NOPB | Texas Instruments
TERM BLK 2POS SIDE ENTRY 5MM PCB | J1, J2, J4, J5, J6, J7, J8, J9, J10, J11, J12, J13, J14, J15 | 1935161 | 14 | 2POS TERM | Phoenix Contact
FERRITE BEAD 300 OHM 0603 1LN | L2 | ILBB0603ER301V | 1 | FERRITE | Vishay Dale
LED GREEN CLEAR 0603 SMD | LED1, LED2 | 150060VS75000 | 2 | GREEN | Wurth Electronics
LED GREEN CLEAR 0603 SMD | LED3 | 150060RS75000 | 1 | RED | Wurth Electronics
Red 620nm LED Indication - Discrete 2.4V 1113 (2835 Metric) | LED4 | QBHP686-RH | 1 | RED | QT-Brightek
SWITCH SPST On-Off 16A (AC) | M39 | R-1-110-C5N-BB | 1 | ON/OFF SWITCH | HONGJU
SWITCH SPST 10mA Panel Mounting | M40, M41, M42, M43, M44, M45, M46 | CPG151101S13 | 7 | UI Panel Switch | Kailh
Switch accessories - Caps RoHS | M47, M48, M49, M50, M51, M52 | 6JBLK | 6 | SWITCH CAP | E-Switch
M3*30 Studs RoHS | M53, M54, M55, M56, M57 | C89822 | 5 | STANDOFFS | LCS
M3 Nut | M58, M59, M60, M61 | C357432 | 4 | M3 NUT | LCS
5V 1.2A Though Hole Power Modules | PS2 | HL06M12S05A | 1 | Isolated PS | LCS-HENIPER
RES SMD 10K OHM 1% 1/4W 1206 | R1, R11, R12, R13, R18, R19, R20, R21, R22, R23, R24, R25, R44, R45, R46, R47, R48, R49, R50 | RC1206FR-07200RL | 19 | 200R0 | Yageo
RES SMD 0 OHM JUMPER 1/10W 0603 | R2, R4, R5, R7, R27, R29, R30, R33, R34, R36, R37, R39 | ERJ-3GEY0R00V | 12 | 0R0 | Panasonic
RES SMD 10K OHM 5% 1/10W 0603 | R3, R8, R9, R10, R26 | RC0603JR-0710KL | 5 | 10K | Yageo
RESISTOR 47 Ohms ±5% 0.1W, 1/10W Chip Resistor 0603 | R6 | CRGCQ0603J47R | 1 | 47R0 | TE Connectivity
RES 20 OHM 1% 1/2W 1206 | R14, R15, R16 | RNCP1206FTD20R0 | 3 | 20R0 | Stackpole Electronics
RES SMD 1.2K OHM 1% 1/4W 1206 | R17 | RC1206FR-071K2L | 1 | 1K2 | Yageo
RES SMD100K OHM 0.5% 1/16W 0603 | R28, R31, R32, R35, R38, R41 | RR0816P-104-D | 6 | 100K | Susumu
Tactile Switch SPST-NO Top Actuated Surface Mount | SW1 | PTS526SM15SMTR2LFS | 1 | Tactle switch | ITT C&K

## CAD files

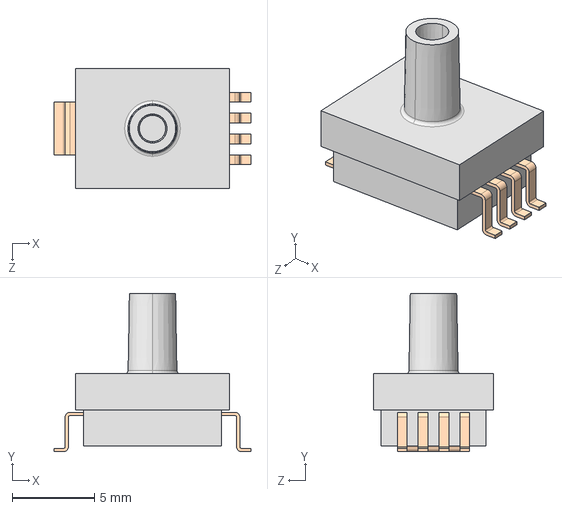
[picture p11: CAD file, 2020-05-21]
3D/User Library-pressure_sensor_mpxm2010.step
12.0 x 9.65 x 7.30 mm

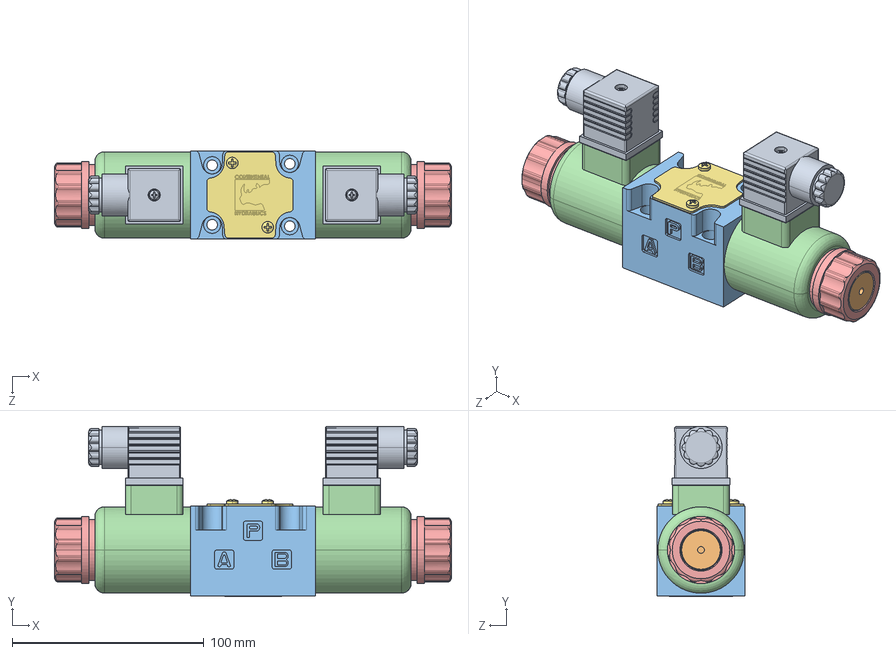
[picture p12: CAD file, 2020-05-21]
Assembly/Continental Hydraulics-VED03M-3 K1 SOL DES C.step
207.0 x 88.9 x 46.0 mm

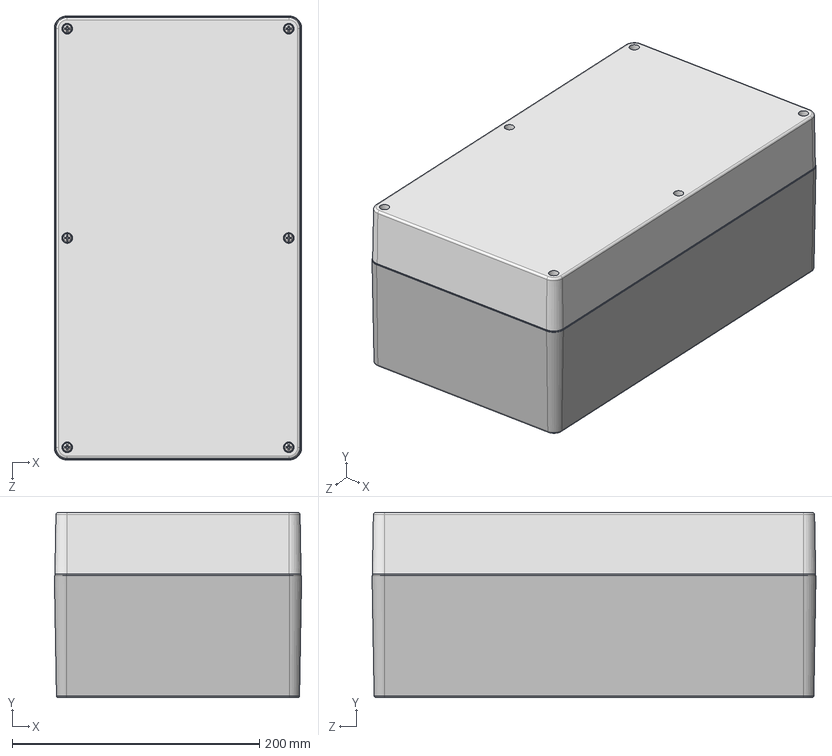
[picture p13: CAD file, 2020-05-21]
Assembly/Enclosure/WP-44.STEP
200.1 x 150.0 x 359.3 mm
W_-44B_WP-44B*15
SCREWS-SSM4-25 x 6
W_-44C_WP-44C*15
W_-44B-PCB_WP-44B*15-PCB

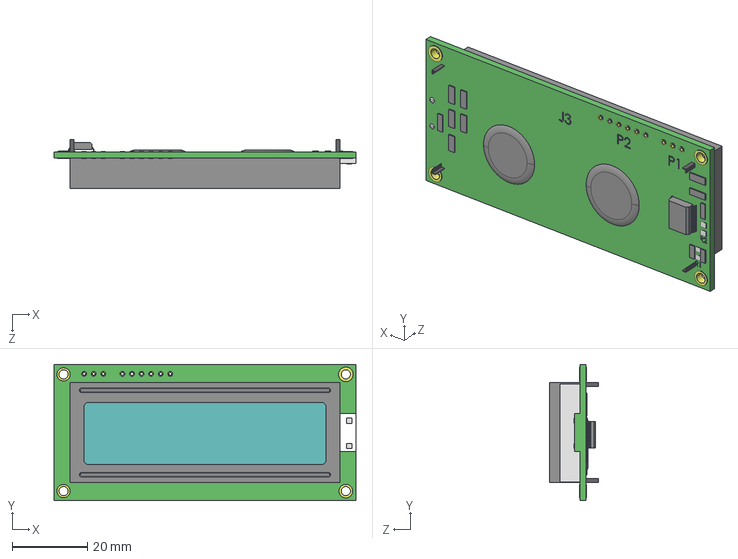
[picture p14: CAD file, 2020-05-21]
3D/User Library-NHD-0216K3Z-FL-GBW-V3.step
80.2 x 36.2 x 13.0 mm

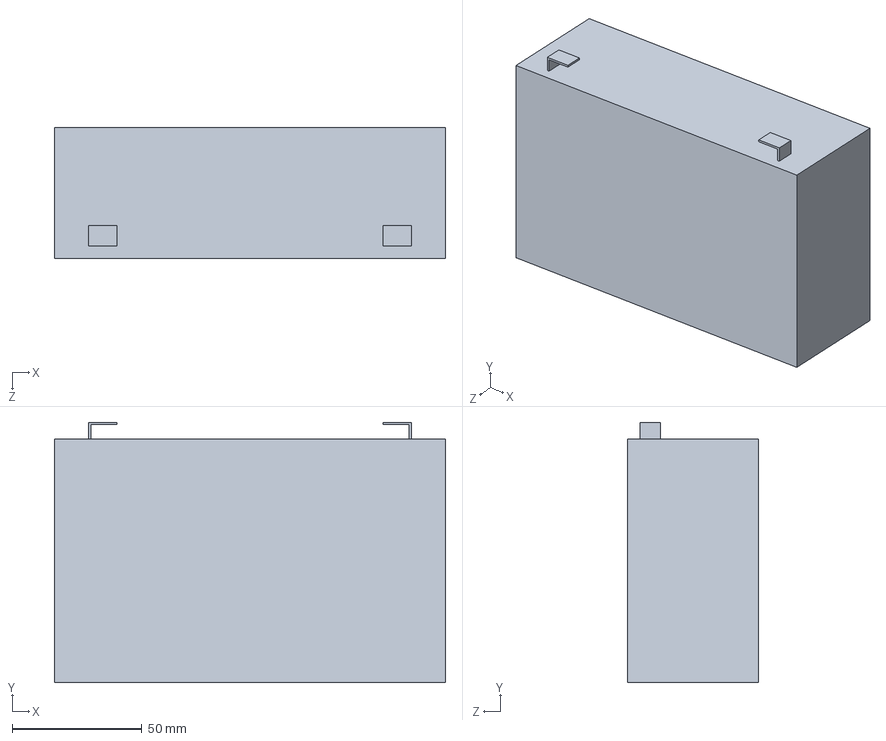
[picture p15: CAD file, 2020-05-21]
Assembly/Battery.SLDPRT
150.7 x 100.3 x 50.3 mm

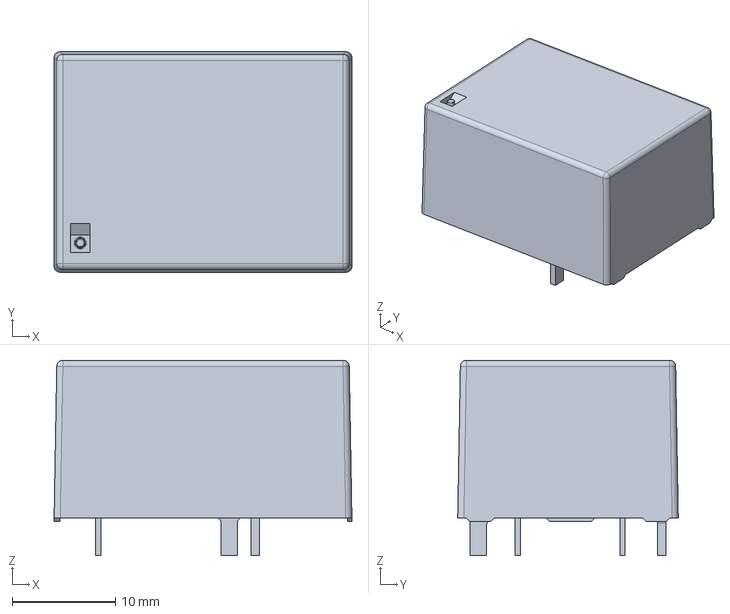
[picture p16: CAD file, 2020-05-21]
3D/c-1558661-3-b-3d.stp
28.9 x 21.4 x 18.9 mm

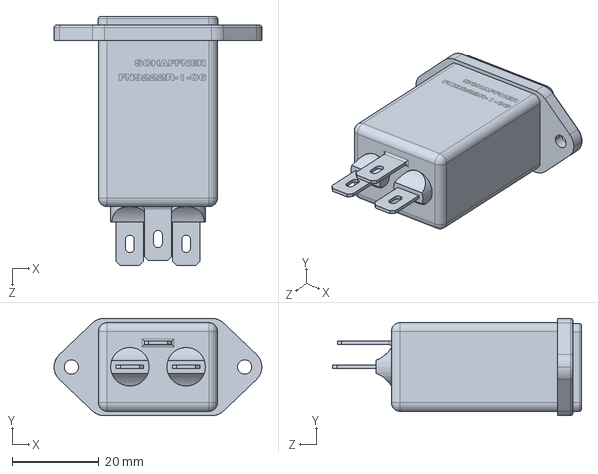
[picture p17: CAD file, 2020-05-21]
Assembly/User Library-Schaffner_FN9222R-1-06_filtered_IEC_inlet.step.SLDPRT
48.0 x 22.5 x 57.5 mm

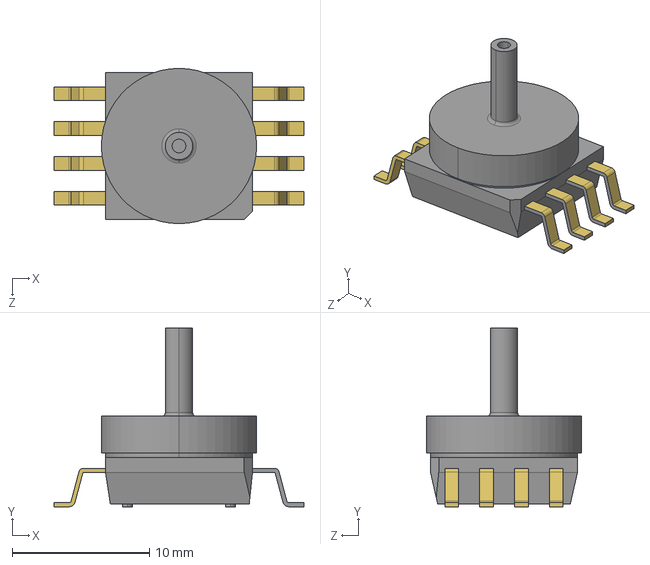
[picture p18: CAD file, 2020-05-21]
3D/User Library-Freescale MPX.step
18.2 x 13.0 x 11.3 mm

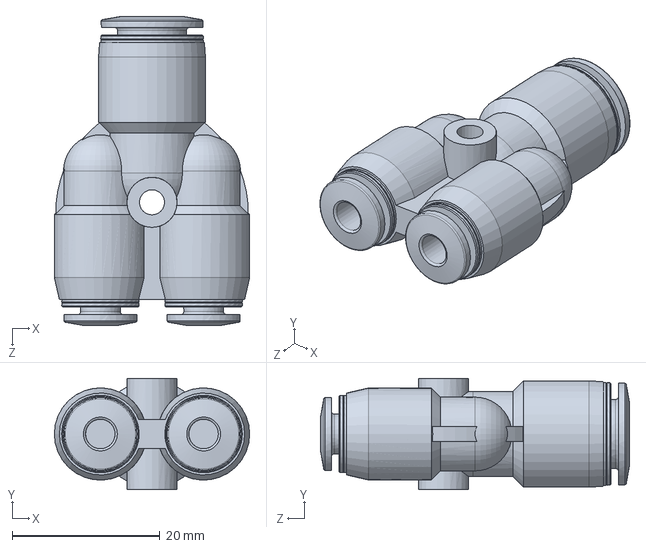
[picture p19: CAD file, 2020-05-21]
Assembly/Y-Fitting.SLDPRT
26.5 x 15.1 x 41.9 mm

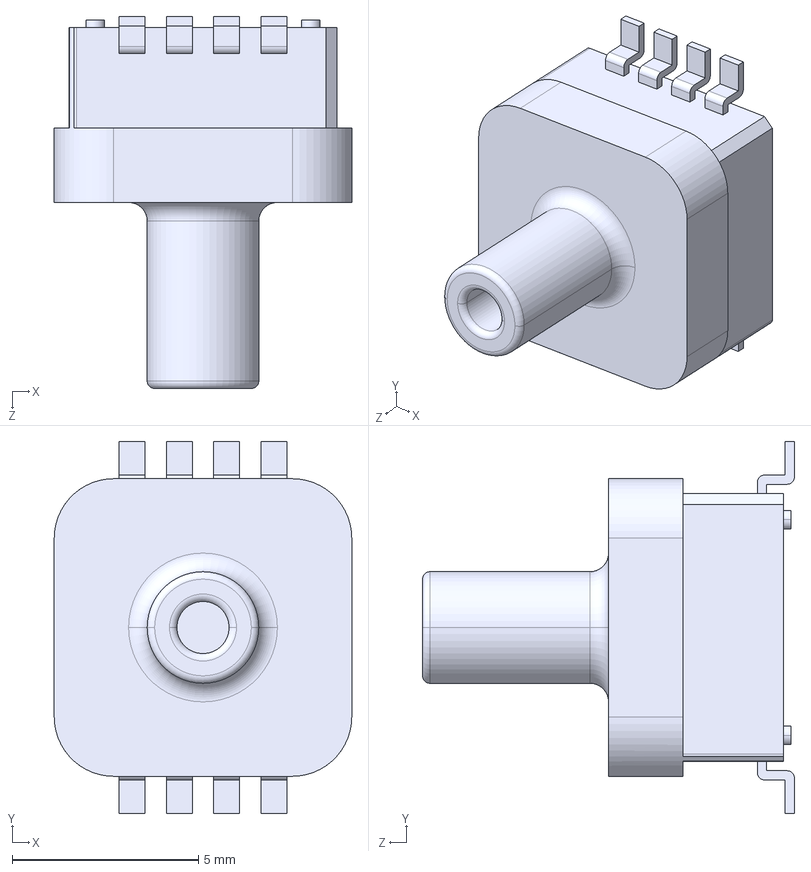
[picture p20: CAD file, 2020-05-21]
3D/User Library-MPXH6115AC6.step
8.00 x 10.00 x 10.0 mm

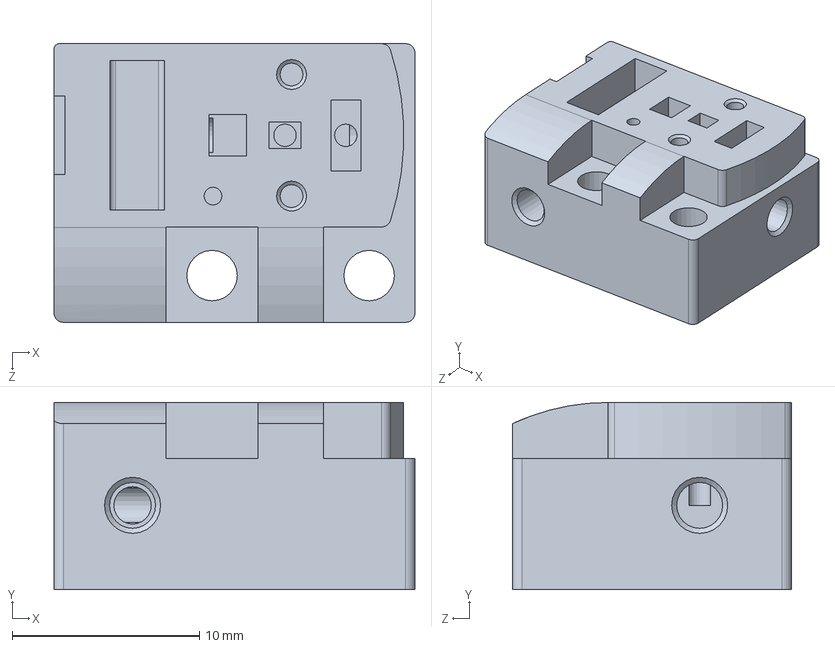
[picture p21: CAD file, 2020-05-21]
Assembly/2-2-Electrovalve-plates.SLDPRT
19.3 x 10.0 x 14.9 mm

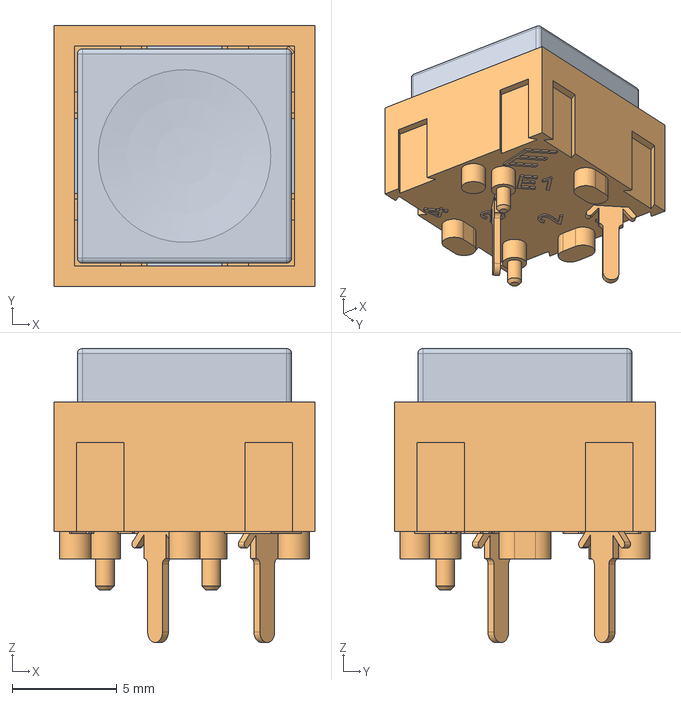
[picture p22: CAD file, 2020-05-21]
3D/320E11xxx.stp
12.4 x 12.4 x 14.1 mm

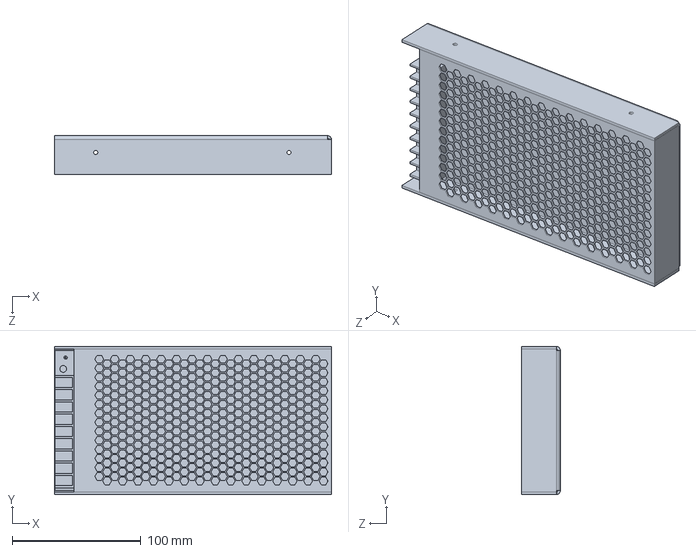
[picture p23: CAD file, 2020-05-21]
Assembly/Fuente meanwell LRS-200-12.SLDPRT
215.0 x 115.0 x 30.0 mm

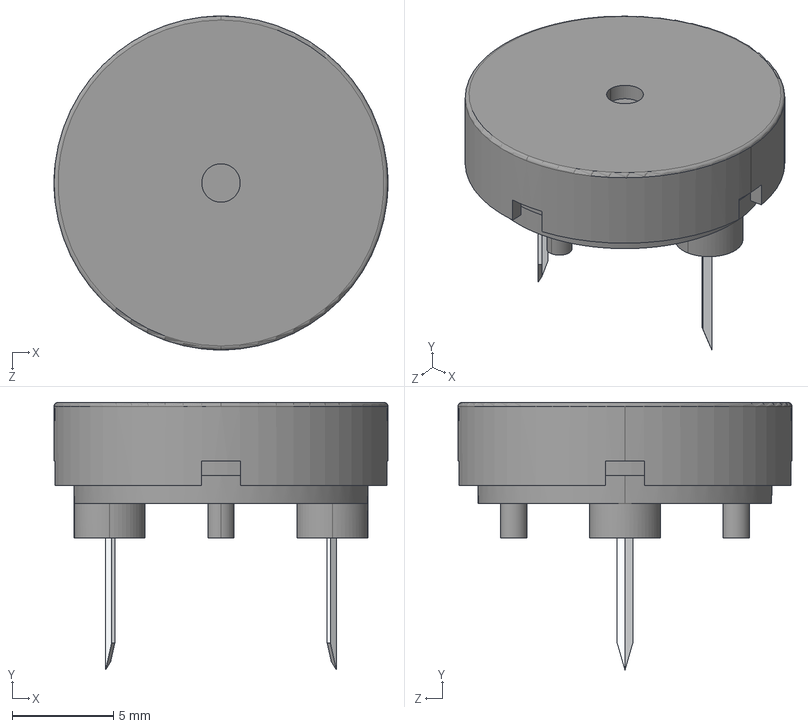
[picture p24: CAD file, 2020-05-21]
3D/CUI_DEVICES_CPT-1667-85T.step
16.5 x 13.2 x 16.5 mm

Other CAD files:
Images Logo/Drawing1.dxf
Assembly/3-2-Electr0valve-plates.SLDPRT
Assembly/3-2-Air-Selonoid-Valve.SLDPRT
Assembly/User Library-Schaffner_FN9222R-1-06_filtered_IEC_inlet.step
Assembly/1-4-4mm Reduction Fitting.SLDPRT
Assembly/2-2-Air-Selonoid-Valve.SLDPRT
Assembly/Compressor.SLDPRT
Assembly/Fitting.SLDPRT
Assembly/LRS-200/Fuente meanwell LRS-200-12.ipt
Assembly/SLA Battery 12V.step
Assembly/STL Files/2-2-Electrovalve-plates.STL
Assembly/STL Files/3-2-Electr0valve-plates.STL

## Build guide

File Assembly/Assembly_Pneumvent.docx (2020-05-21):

# PNEUMVENT SYSTEM DIASSEMBLED

Please Note that the following document shows the components required for assembling Pneumvent (the ventilator). This document doesn’t show the spirometer kit (how the machine is connected to the patient) but rather shows the modularity of the machine , ease of assembly, maintenance and ease of remove and installation of the battery.

Please reference the block diagram section for how to hookup the machine to the patient.

# Front Section

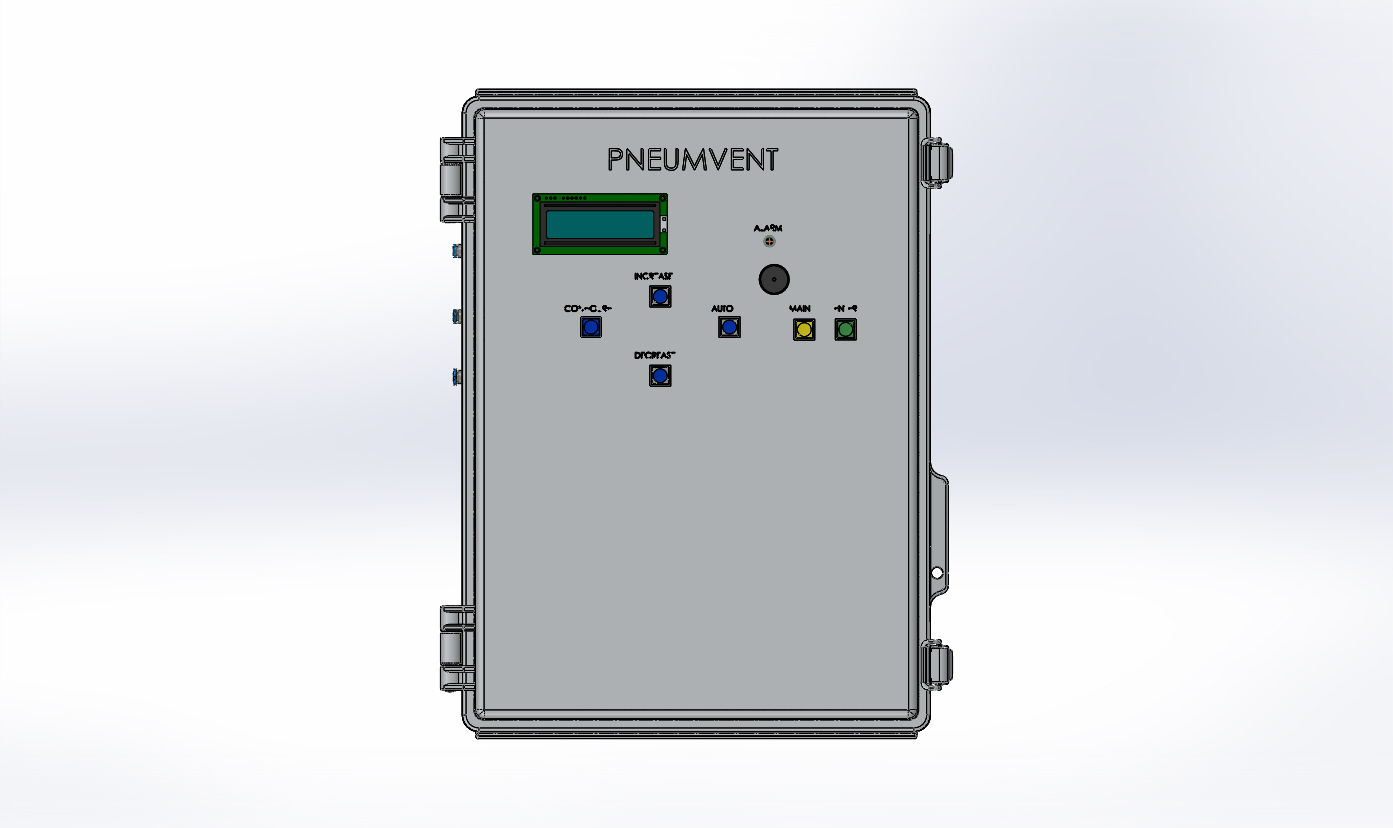
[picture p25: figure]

# Control Panel- Human Machine Interface

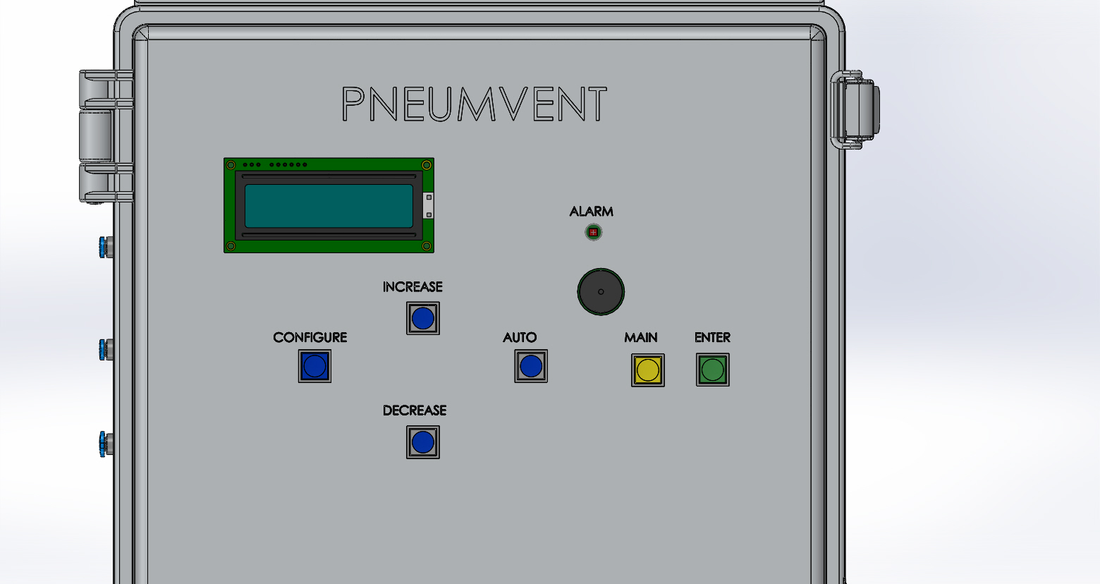
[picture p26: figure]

# Pneumatic System Inlets

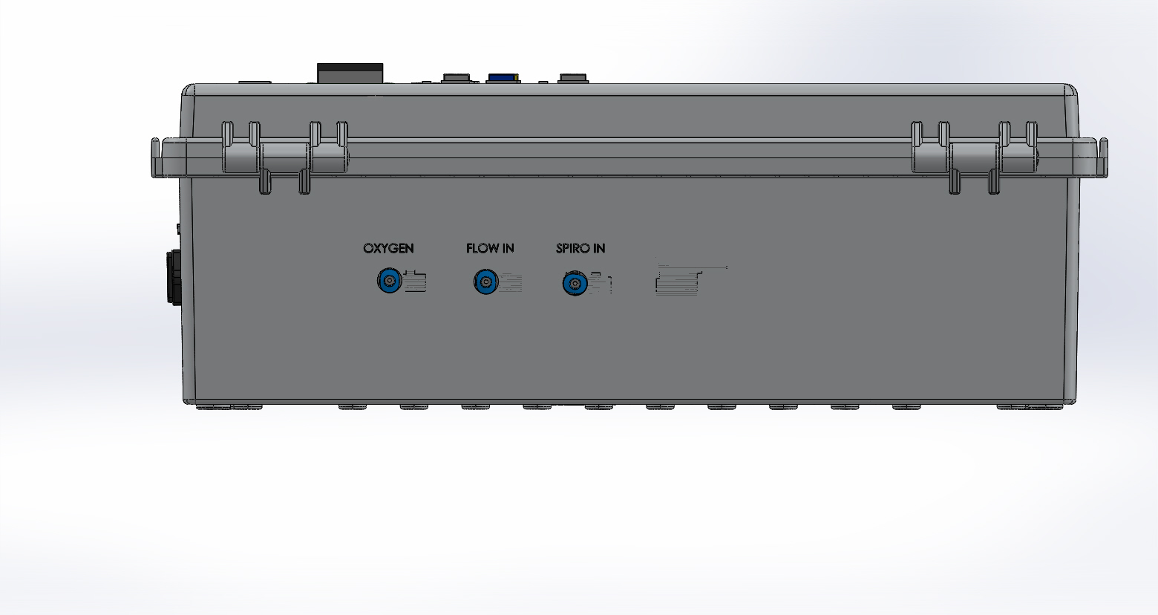
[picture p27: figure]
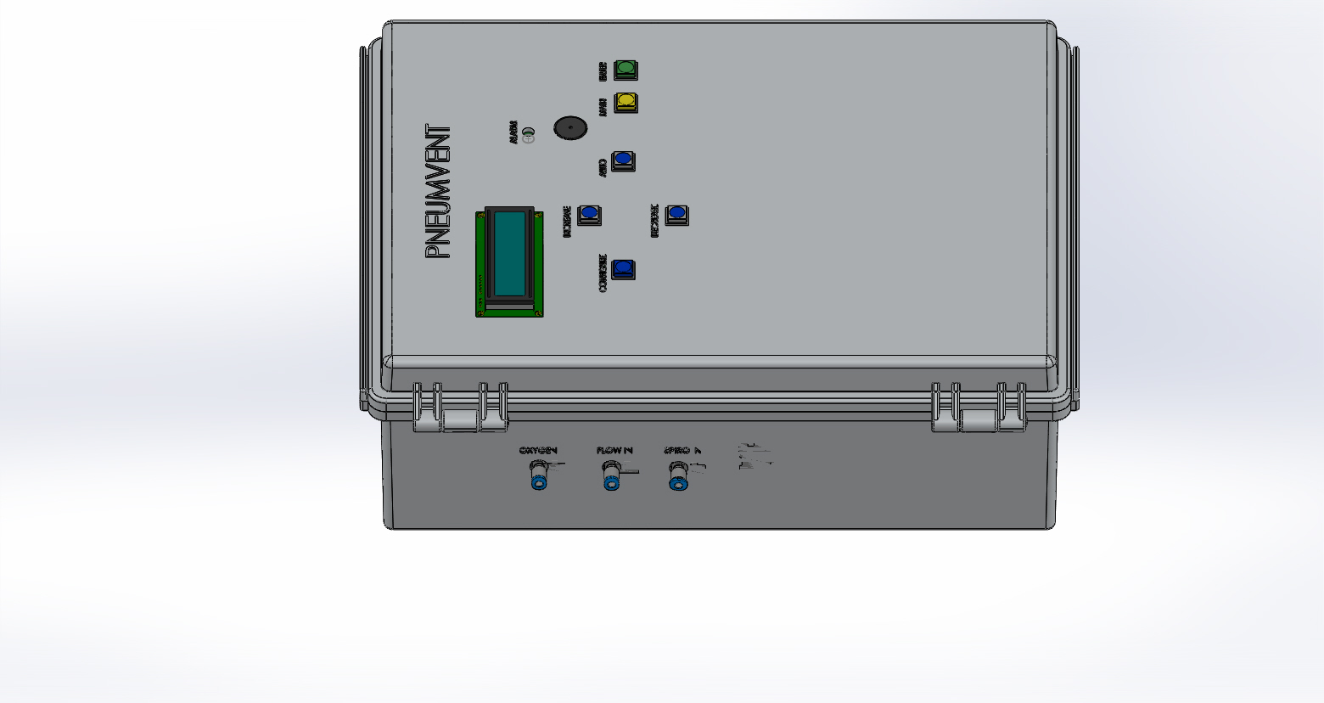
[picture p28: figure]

# 110/220 VAC Power Receptacle Input

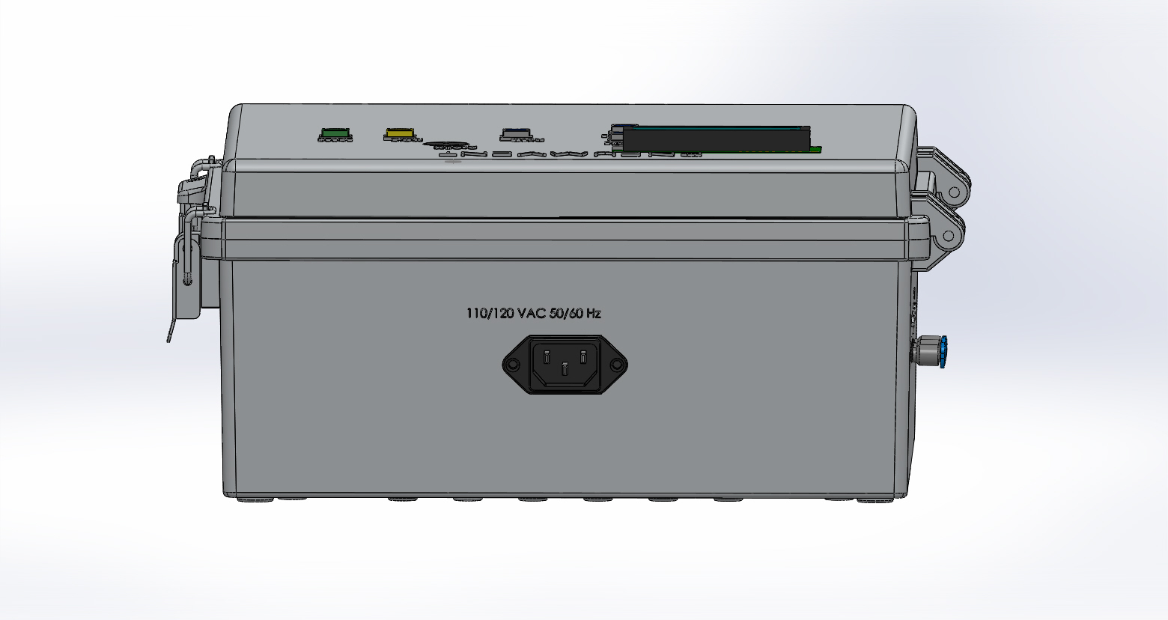
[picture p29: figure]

# Inside of Enclosure

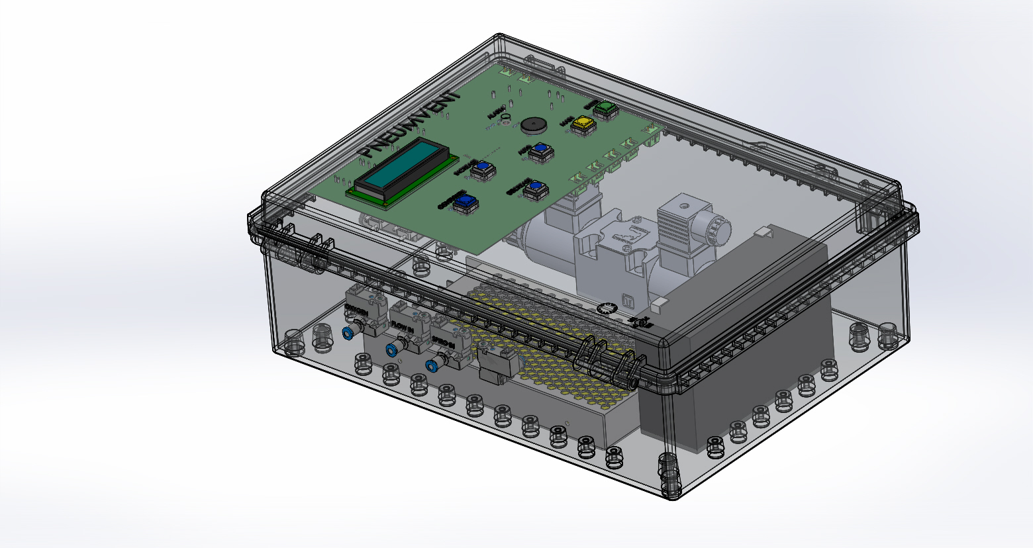
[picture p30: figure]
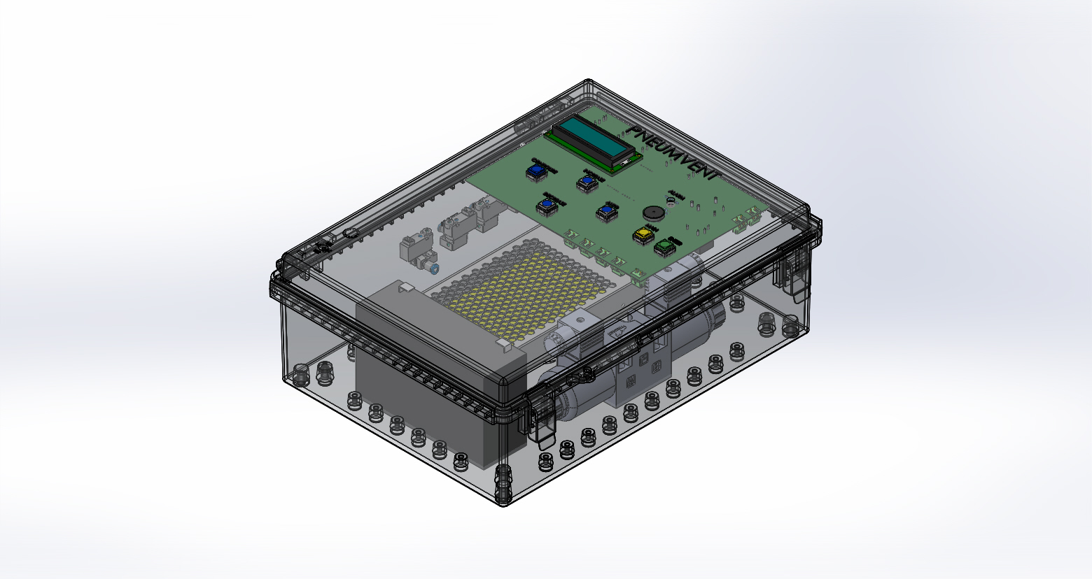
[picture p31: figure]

# Pneumatic System

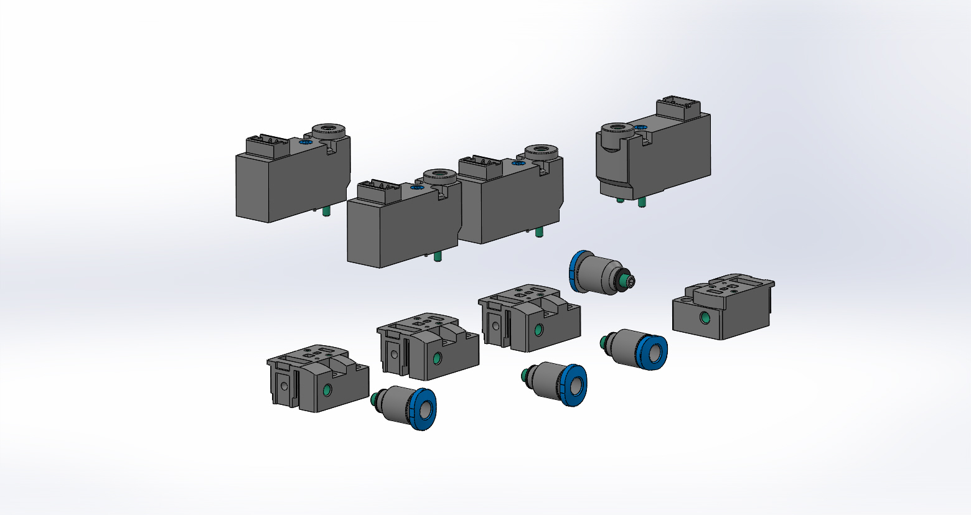
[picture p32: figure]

Agorize- Code of Life VentilatorHussam Eidinfo@hussameid.com

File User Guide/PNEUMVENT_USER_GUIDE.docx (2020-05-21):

# PNEUMVENT

# USER GUIDE

# Human Machine Interface

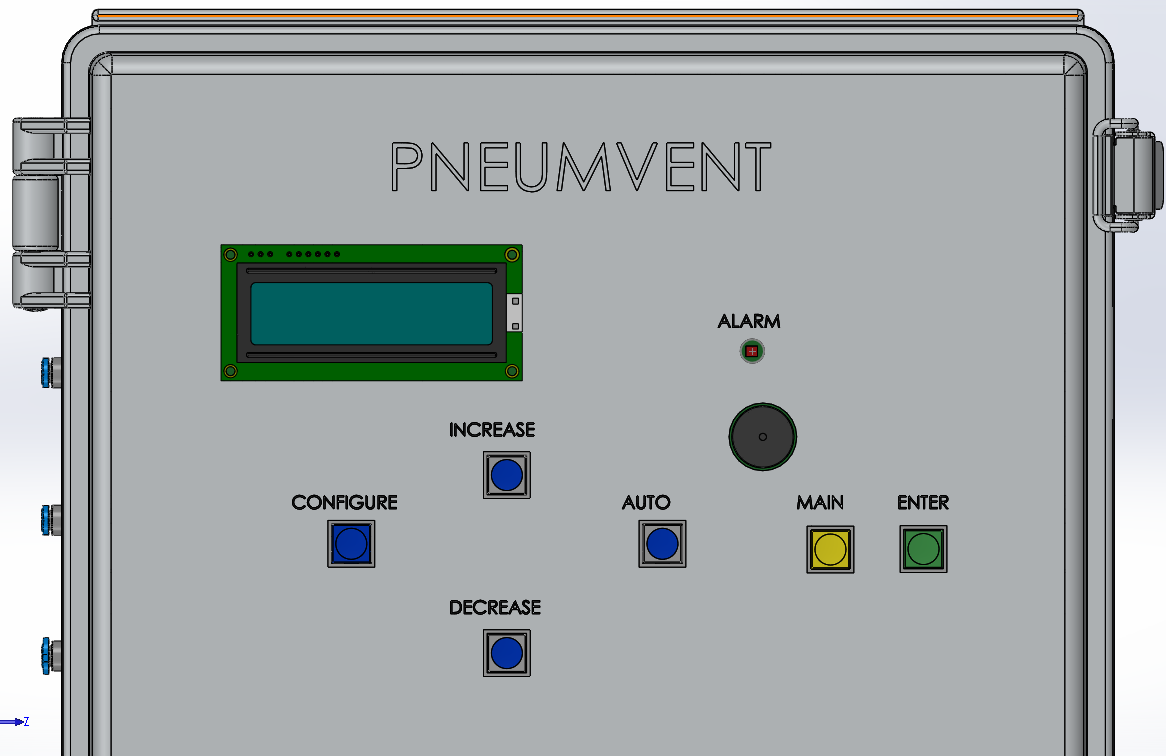
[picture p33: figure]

The system uses and LCD display to display system parameters as well as having six buttons for the user to interact with the system. The functions for the buttons are described below:

CONFIGURE BUTTON- It always the user to change the mode of operation of the system. At any time the user can change three control modes , namely:

1- Pressure
2- Frequency
3- Assisted

All three control modes have 13 parameters that are displayed or can be modified, namely:

1- Mode of Operation: Changes the control mode of the system to Pressure, Frequency or Assisted mode
2- Temperature: Displays the current system temperature inside the enclosure. This is necessary to ensure that the temperature drift is compensated for when measuring the sensor values
3- Lower Tank Pressure: Changes the lower pressure threshold for the oxygen tank. If the pressure drops below the specified value the alarm would go off.
4- Tank High Pressure- Changes the upper pressure threshold for the oxygen tank. If the pressure drops below the specified value the alarm would go off.
5- Lung Pressure- Displays the measured lung pressure
6- Lower Lung Pressure: Modifies the lower limit for the lung pressure. If the pressure drops below the specified value the alarm would go off.
7- Higher Lung Pressure: Modifies the upper limit for the lung pressure. If the pressure drops below the specified value the alarm would go off.
8- Inspiration Percentage: Modifies the inspiration percentage in a breathing cycle. This option is only available under Frequency Mode
9- Respiration Time: Modifies the patient’s total breaths per minute. This option is only available under Frequency Mode
10- FiO2: Modifies the total O2 percentage in the breathing mixture.
11- Mixture Pressure: Displays the total air pressure going into the patient
12- Pressure Unit: Converts the displayed pressure units to H20 cm, PSI, KPA,mbar and Hg mm.
13- Temperature: Converts the displayed pressure to Celsius or Fahrenheit

ENTER BUTTON-It is used to modify the system parameters. When the button is pressed a cursor on the LCD screen starts blinking. Whenever a cursor starts blinking you can modify the required parameters. The new parameters that you entered is only saved after you press the ENTER button again.

INCREASE/DECREASE BUTTON- Pressing either buttons will display one of the 13 parameters mentioned above. If the ENTER button is pressed and the cursor is blinking , pressing the INCREASE/DECREAE button will increase or decrease the value of the blinking cursor.

MAIN BUTTON- Returns to the main display page (HOME) which displays most important parameters on a single screen, namely:FiO2, Mixture Pressure, and respiration time.

AUTO BUTTON- Displays system parameters one at a time within 7 second interval.

# Breathing Controller:

Pneumvent can support 5 classifications of breathing which is controlled by the MCU. Those breathing classifications are displayed in the table below.

Breathing Classification | Description
Time Cycle | Inspiration and expiration time is set at a certain timed threshold
Pressure Cycle | Inspiration cycle stops once a pressure threshold is reached
Flux Cycle | Inspiration cycle stops when aspiration flux drops below a pressure threshold
Volume Cycle | Inspiration cycle stops once a certain volume of gas has been inhaled
Custom Cycle | Any of the above cycles combined together

# Alarm System

The alarm system is one of the critical indicators of Pneumvent and an alarm condition occurs when a set of fault condition is reached. A fault condition is reached when the sensor parameters are not within a predefined threshold. An example of an alarm triggering condition is when Pneumvent doesn’t detect an inspiration within a certain period of time.

In case of an alarm condition, a bright red LED on the front panel starts flashing as well as an audible buzzer goes off at 90dB. The volume level can be adjusted but only before the unit is built.

Agorize: Code Life VentilatorHussam Eidinfo@hussameid.com

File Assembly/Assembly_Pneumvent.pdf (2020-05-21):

Agorize- Code of Life Ventilator | Hussam Eid | info@hussameid.com

## PNEUMVENT SYSTEM DIASSEMBLED

Please Note that the following document shows the components required for assembling Pneumvent (the ventilator). This document doesn’t show the spirometer kit (how the machine is connected to the patient) but rather shows the modularity of the machine , ease of assembly, maintenance and ease of remove and installation of the battery.
Please reference the block diagram section for how to hookup the machine to the patient.

## Front Section

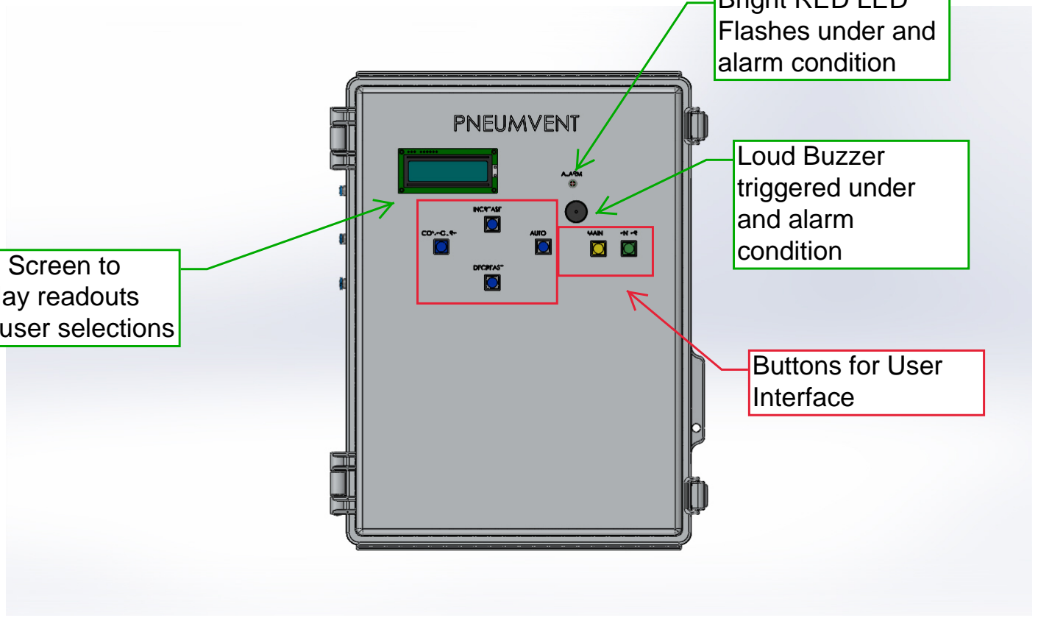
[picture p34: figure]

## Control Panel- Human Machine Interface

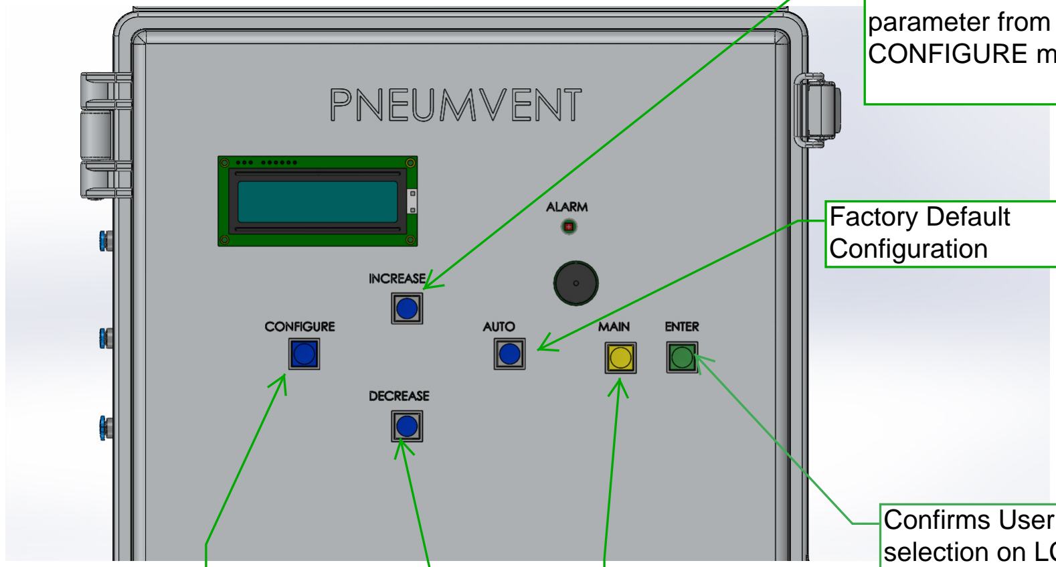
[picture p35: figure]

## Pneumatic System Inlets

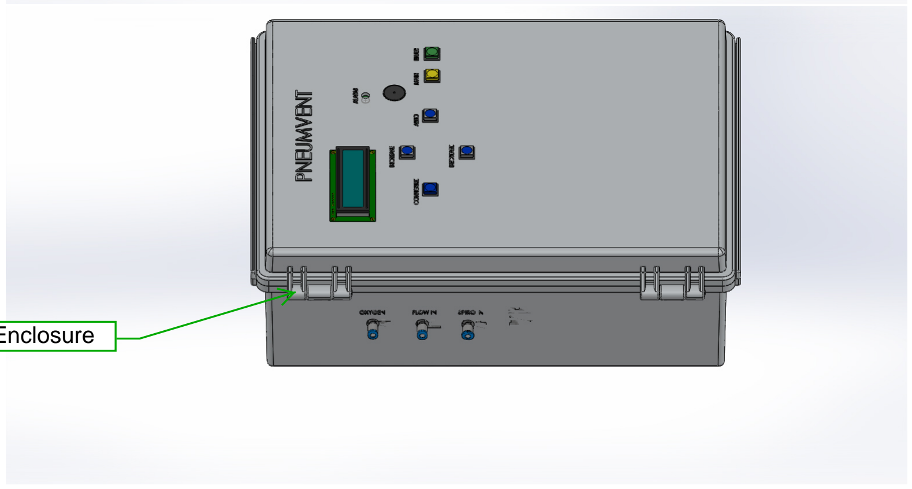
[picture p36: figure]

## 110/220 VAC Power Receptacle Input

## Inside of Enclosure

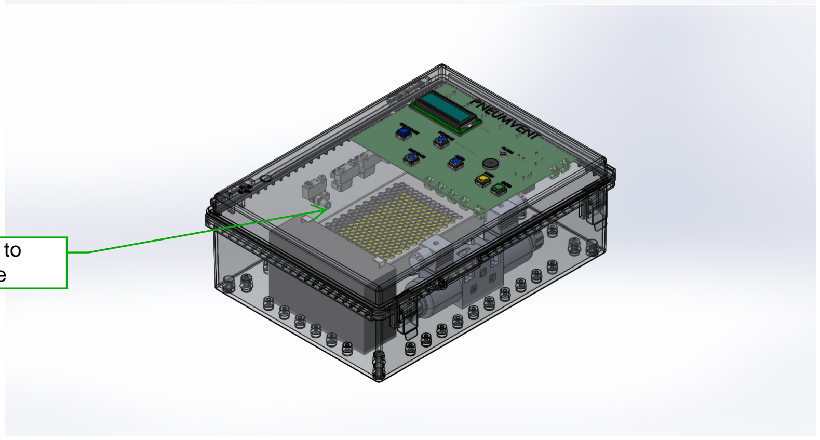
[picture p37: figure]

## Pneumatic System

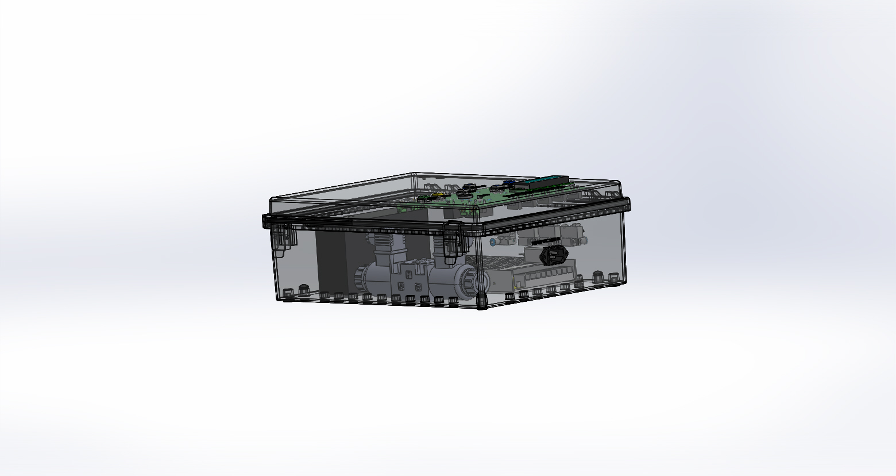
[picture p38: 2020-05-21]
Assembly/Assem8.JPG

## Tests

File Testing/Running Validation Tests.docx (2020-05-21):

# Running Validation Tests

Pneumvent is a well-integrated device that constantly compare all of the sensors and actuators data to each other ensuring that all parameters are within a predefined threshold. However, it is important to run validation tests often since having the device report a failure while running on a patient could be catastrophic as compared to verifying the device functionality beforehand.

This section describes how to run a validation test as well as the frequency of validation.

# How often should I run the validation test?

The validation test should run every time a component is removed/replaced from the device, this includes the HME, filter, battery, respiratory tube and anything that is considered part of Pneumvent.

This ensures that any of the components added such as breathing tube are not defective. For instance if the breathing tube has a leak/hole Pneumvent will be able to tell and throw an alarm condition.

# How do I run the validation test on Pneumvent?

Running the validation test is automated on Pneumvent and it is runs on a series of self-tests by the click of a set of buttons. However, during one of the self-tests conditions, Pneumvent will require the intervention of a user/technician to simulate the self-assisted operation. This is discussed below.

# Control Panel Preview

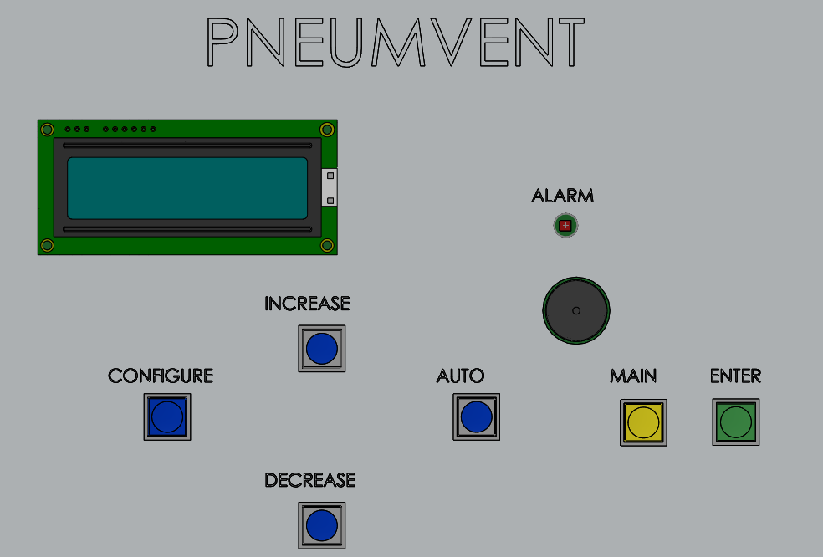
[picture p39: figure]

## Process:

1- Plug in Pneumvent into the main wall socket and ensure a “Beep” sounds for three seconds
2- Ensure the LCD displays “STAND-BY MODE”

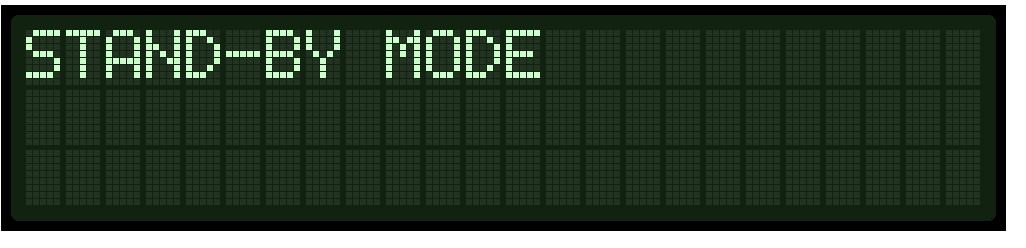
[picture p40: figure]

3- Next Press the “AUTO” button for 10 seconds
4- The device will display

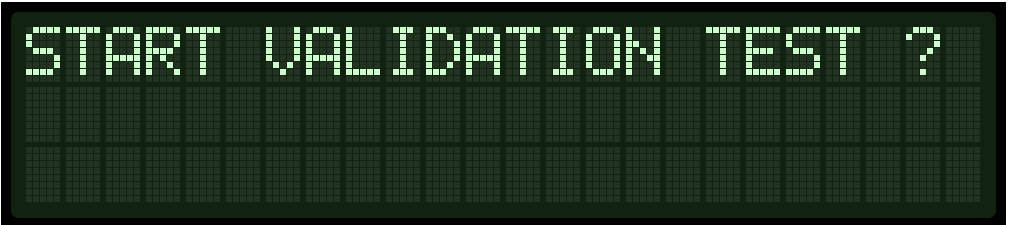
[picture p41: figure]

5- Press the “ENTER” button
6- The validation test will run as follows:
- Lung Pressure test

“PASS” will be displayed with a short beep, or “FAIL” with a constant beep

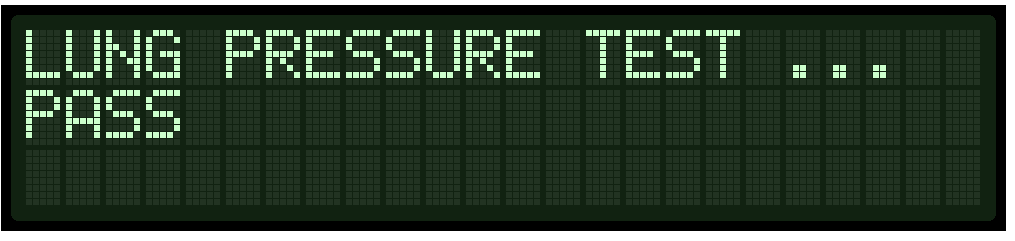
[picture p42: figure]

- Breathing Rate Test

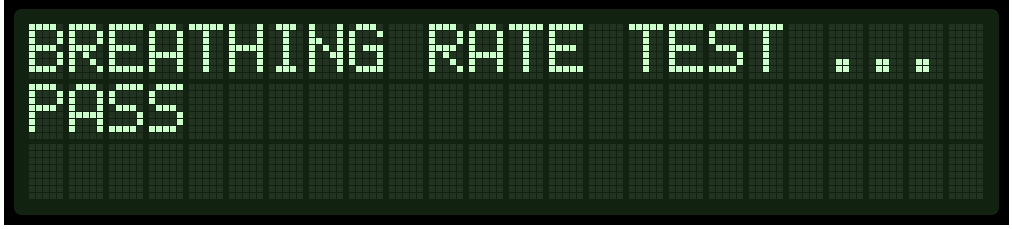
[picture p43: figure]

“PASS” will be displayed with a short beep, or “FAIL” with a constant beep

- Inspiration/Expiration Ratio test (I:E test)

“PASS” will be displayed with a short beep, or “FAIL” with a constant beep

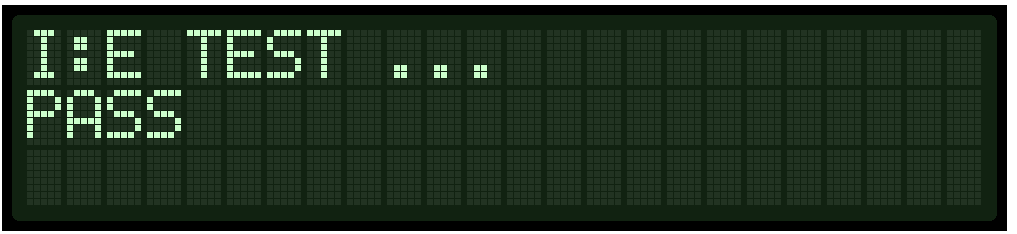
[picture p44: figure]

- Air Mixture Pressure Test

“PASS” will be displayed with a short beep, or “FAIL” with a constant beep

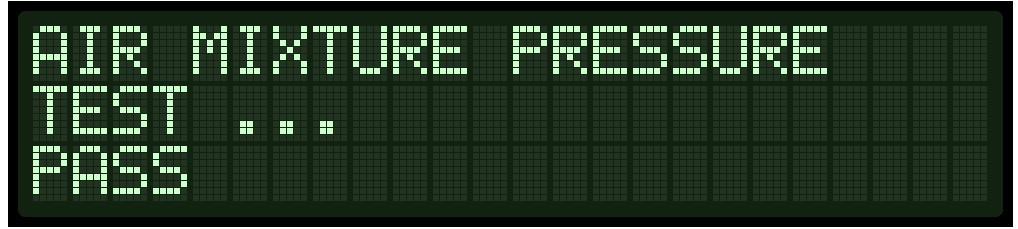
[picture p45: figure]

- The Operation mode of trigger will star running 5 seconds after the screen:

“PASS” will be displayed with a short beep, or “FAIL” with a constant beep

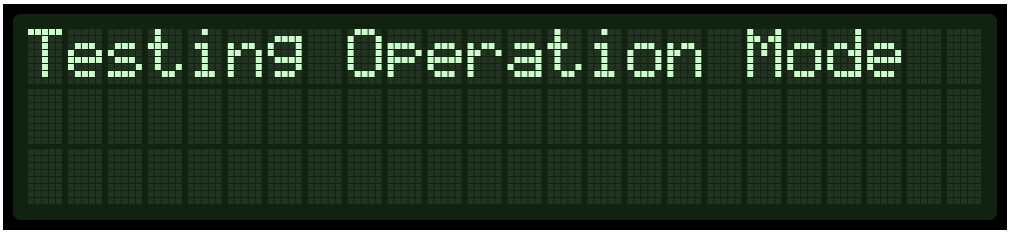
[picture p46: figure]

- Testing Pressure Triggered Mode:

“PASS” will be displayed with a short beep, or “FAIL” with a constant beep

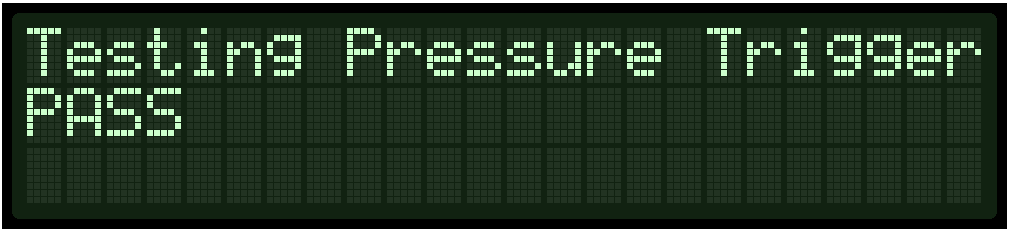
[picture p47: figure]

- Testing Time Triggered Mode:

“PASS” will be displayed with a short beep, or “FAIL” with a constant beep

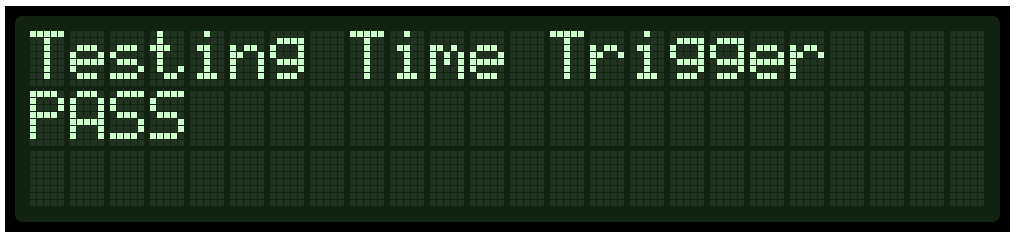
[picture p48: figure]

- Testing Assisted Pressure Mode, note in this mode user assistance is required:


- After reaching this screen the user is required to simulate a breathing trigger by creating a vacuum on the breathing tubes. Once can achieve that by placing the palm of their hands on top of the tube opening creating a strong seal and quickly lifting their palm. As a result a suction pressure is simulated. The screen updates to :


- Next create an exhalation simulation by doing the reverse with your palm and pushing air into the tube (or you can blow into the tube), the screen updates to:


- The validation test is complete at this point and the screen updates to:


This means that the validation test is complete and the device is ready to use!

Agorize-Code LifeHussam Eidinfo@hussameid.com

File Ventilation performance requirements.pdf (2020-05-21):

VENTILATION PERFORMANCE

1. Pressure controlled
1. Inspiratory pressure up to 40cmH2O
2. Expiratory pressure up to 20cm H2O
3. Respiratory rate from 5-40 breaths a minute
4. Measurement of tidal volume at the Y piece
2. FiO2 from 20% to 100% in discreet steps of 10%
3. Triggering—timed or patient-effort triggered
4. Connect to standard masks and tubes
5. Connect to standard oxygen connectors
6. Accuracy (<10% for volumes and pressure, to 1 breath a minute for rate
7. Can work on internal battery for >180 min
8. Oxygen concentration NOT mandatory, recommended

PATIENT SAFETY
ALARMS OR LIMITS
1. Minute Ventilation (low/High) alarm
2. Peak pressure, Low expiratory pressure and/or disconnection alarm
3. Low expiratory pressure
4. Oxygen concentration
5. Non-rebreathing valves
DEVICE SAFETY
1. Electrical safety requirements
2. Fire safety (i.e., pure O2 flowing) INFECTION CONTROL
1. HEPA filtered inlet and outlet
2. Easy-to-clean surfaces
DESIGN REQUIREMENTS
USER INTERACTION
1. Simple to use--must not require specialized training
2. Modular, with known failure potential for each component
3. Easy to maintain (related to modularity)
4. Settings legible from 1m
5. Clear flow directions
MATERIAL AND MANUFACTURABILITY
1. Widely available material (e.g. 3D printable filaments, plastic/metal sheets)
2. Can be built locally using either simple tools or rapid prototyping (i.e. 3D printing, CNC, etc.)
3. Only eligible material allowed (see list to exclude)
OPERATIONAL REQUIREMENTS
1. Both 110V and 220V
TESTING, CALIBRATION, AND MAINTENANCE REQUIREMENTS
1. Tests to calibrate and validate volume and pressure settings
2. Tests to verify limits and alarms
3. Illustrated and clear diagram for taking apart, replacing, and rebuilding the device safely

REFERENCES
1. ISO 80601-2-12:2020 Standard for Medical electrical equipment — Part 2-12: Particular requirements for basic safety and essential performance of critical care ventilators

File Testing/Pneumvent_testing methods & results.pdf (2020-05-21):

Parameter Tested | Description | Testing Method | Value Range | Default Value | Error Message Displayed on LCD


Lung Pressure (Low & High) | The range of pressure in the the patient's Lung. If the pressure is lower lower than the limit the inspiration valve turns ON until pressure range is achieved | Run self‐test without hooking up the respirator tubes to patient , within 10 seconds Alarm will beep displaying either "Pressure too low" or "Pressure too high". That is achieved by comparing the default lung pressure values to the expected values, if the values are out of the threshold then an alarm condition is triggered. | 0‐100 cmH20 | 20‐40 cmH20
Breathing Rate | The rate at which the breathing takes place per minute | Run self‐test without hooking up the respirator tubes to patient, within 10 seconds alarm will beep displaying either "low respiration rate" or "high respiration rate". This is done by comparing the pressure at the mixture valve to the lung pressure, if there is no change it means no inhalation or exhalation has taken place and ana alarm condition will be triggered. | 5‐18 breaths/min | 14 breath/min
Inspiration/Expiration (I:E) ratio | The ratio of inspiration to expiration time (expressed as percentage) | Run self‐test without hooking up the respirator tubes to patient, , within 10 seconds alarm will beep displaying either "inspiration missed" or "expiration missed" . This done if the pressure at the inhalation or exhalation tubes remains the same after a set amount of time (Breathing rate). If the pressure doesn't change an alarm condition is triggered. | 20%‐70% | 50%


Air Mixture Pressure | The range of pressure of air avaialble for the patient to inhale (Pure oxygen + Compressed Air) | The FiO2 parameter sets the ratio of oxygen to compressed air from which the self‐test uses that value and compares it to the output. If the output is lower than expected FiO2 air mixture pressure the alarm will beep displaying "Low FiO2 Pressure" it is caused by either the oxygen tank going low or the air compressor getting faulty | 0‐200 PSI | 50 PSI
Temperature | Checks that the temperature of the unit is within operation (i.e ‐20 Celcius to 80 Celcius). This is the internal temperature of the device | If the internal temperature of the enclosure exceeds the temperature range the device will issue"extreme Temperature" error. Under either condition the device will not run. | (‐20‐80 )Celcius | 25 Celcius

Pneumvent Test Methods and Test Results


Operation Mode

Ensures that all three modes of operation of the ventilator are operational . i.e. Assisted, pressure and time triggered

The device will trigger the conditions of pressure and time and compare the output to the pressure valves, if the expected pressures are not reached it means one of the above conditions are faulty. Assisted mode is the only condition that requires user input (not self‐tested) and the
user is required to quickly create a vaccum in the tube by
placing their palm of the hand and quickly removing it from
the surface opening of the respiration tube | Pressure Mode | Pressure Mode

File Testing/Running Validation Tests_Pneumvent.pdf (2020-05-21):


Agorize-Code Life | Hussam Eid | info@hussameid.com

## Running Validation Tests

Pneumvent is a well-integrated device that constantly compare all of the sensors and actuators data to each other ensuring that all parameters are within a predefined threshold. However, it is important to run validation tests often since having the device report a failure while running on a patient could be catastrophic as compared to verifying the device functionality beforehand.

This section describes how to run a validation test as well as the frequency of validation.

## How often should I run the validation test?

The validation test should run every time a component is removed/replaced from the device, this includes the HME, filter, battery, respiratory tube and anything that is considered part of Pneumvent.

This ensures that any of the components added such as breathing tube are not defective. For instance if the breathing tube has a leak/hole Pneumvent will be able to tell and throw an alarm condition.

## How do I run the validation test on Pneumvent?

Running the validation test is automated on Pneumvent and it is runs on a series of self-tests by the click of a set of buttons. However, during one of the self-tests conditions, Pneumvent will require the intervention of a user/technician to simulate the self-assisted operation. This is discussed below.

## Control Panel Preview

### Process:

1- Plug in Pneumvent into the main wall socket and ensure a “Beep” sounds for three seconds 2- Ensure the LCD displays “STAND-BY MODE”

3- Next Press the “AUTO” button for 10 seconds 4- The device will display


5- Press the “ENTER” button
6- The validation test will run as follows:
- Lung Pressure test
“PASS” will be displayed with a short beep, or “FAIL” with a constant beep
- Breathing Rate Test
“PASS” will be displayed with a short beep, or “FAIL” with a constant beep


- Inspiration/Expiration Ratio test (I:E test)
“PASS” will be displayed with a short beep, or “FAIL” with a constant beep
- Air Mixture Pressure Test
“PASS” will be displayed with a short beep, or “FAIL” with a constant beep
- The Operation mode of trigger will star running 5 seconds after the screen: “PASS” will be displayed with a short beep, or “FAIL” with a constant beep
- Testing Pressure Triggered Mode:
“PASS” will be displayed with a short beep, or “FAIL” with a constant beep
- Testing Time Triggered Mode:
“PASS” will be displayed with a short beep, or “FAIL” with a constant beep

- Testing Assisted Pressure Mode, note in this mode user assistance is required:


- After reaching this screen the user is required to simulate a breathing trigger by creating a vacuum on the breathing tubes. Once can achieve that by placing the palm of their hands on top of the tube opening creating a strong seal and quickly lifting their palm. As a result a suction pressure is simulated. The screen updates to :


- Next create an exhalation simulation by doing the reverse with your palm and pushing air into the tube (or you can blow into the tube), the screen updates to:


- The validation test is complete at this point and the screen updates to:

This means that the validation test is complete and the device is ready to use!

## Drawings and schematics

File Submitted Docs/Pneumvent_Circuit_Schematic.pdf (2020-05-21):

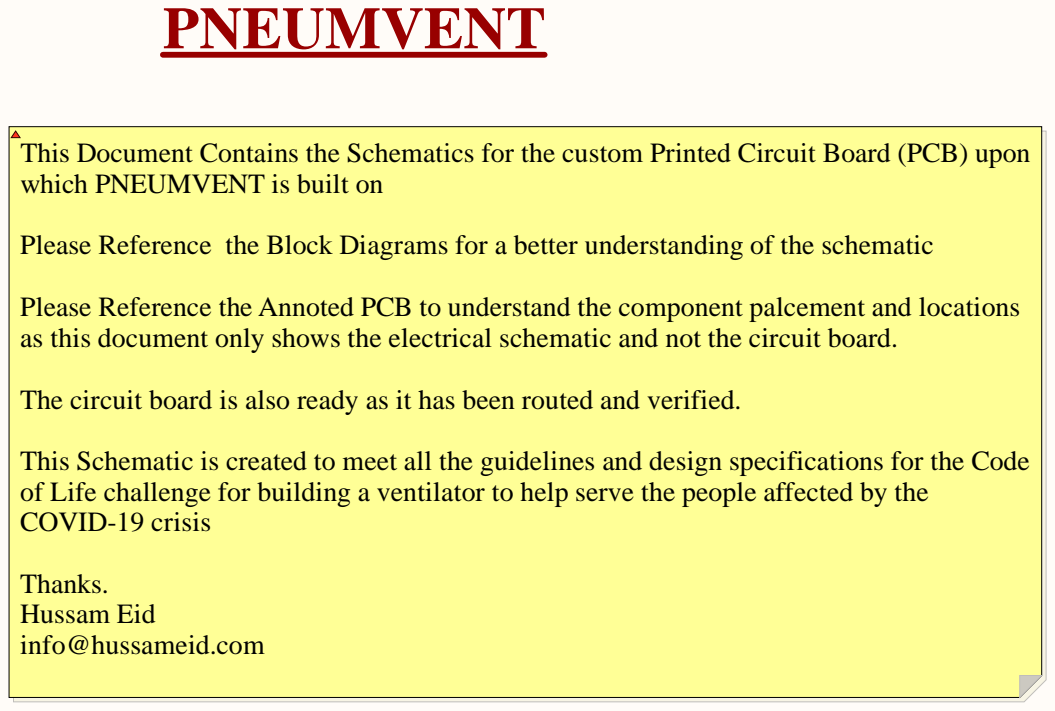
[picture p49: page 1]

This Document Contains the Schematics for the custom Printed Circuit Board (PCB) upon
which PNEUMVENT is built on

Please Reference the Block Diagrams for a better understanding of the schematic

Please Reference the Annoted PCB to understand the component palcement and locations
as this document only shows the electrical schematic and not the circuit board.

The circuit board is also ready as it has been routed and verified.

This Schematic is created to meet all the guidelines and design specifications for the Code
of Life challenge for building a ventilator to help serve the people affected by the
COVID-19 crisis

Hussam Eid (info@hussameid.com)

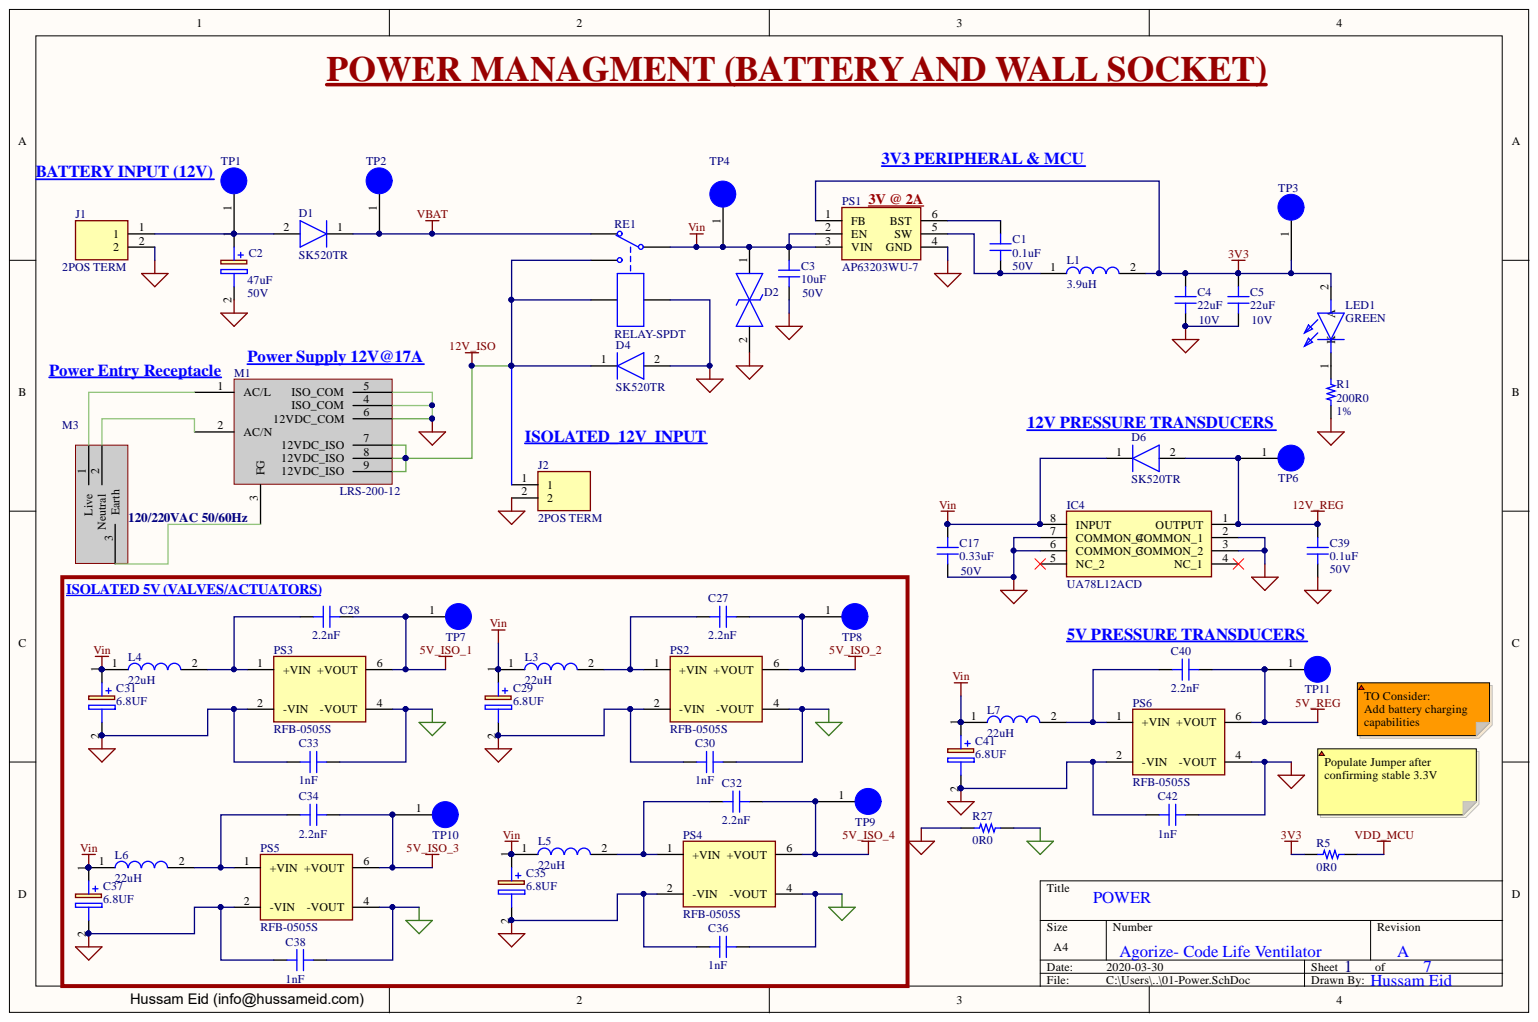
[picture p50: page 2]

POWER MANAGMENT (BATTERY AND WALL SOCKET)

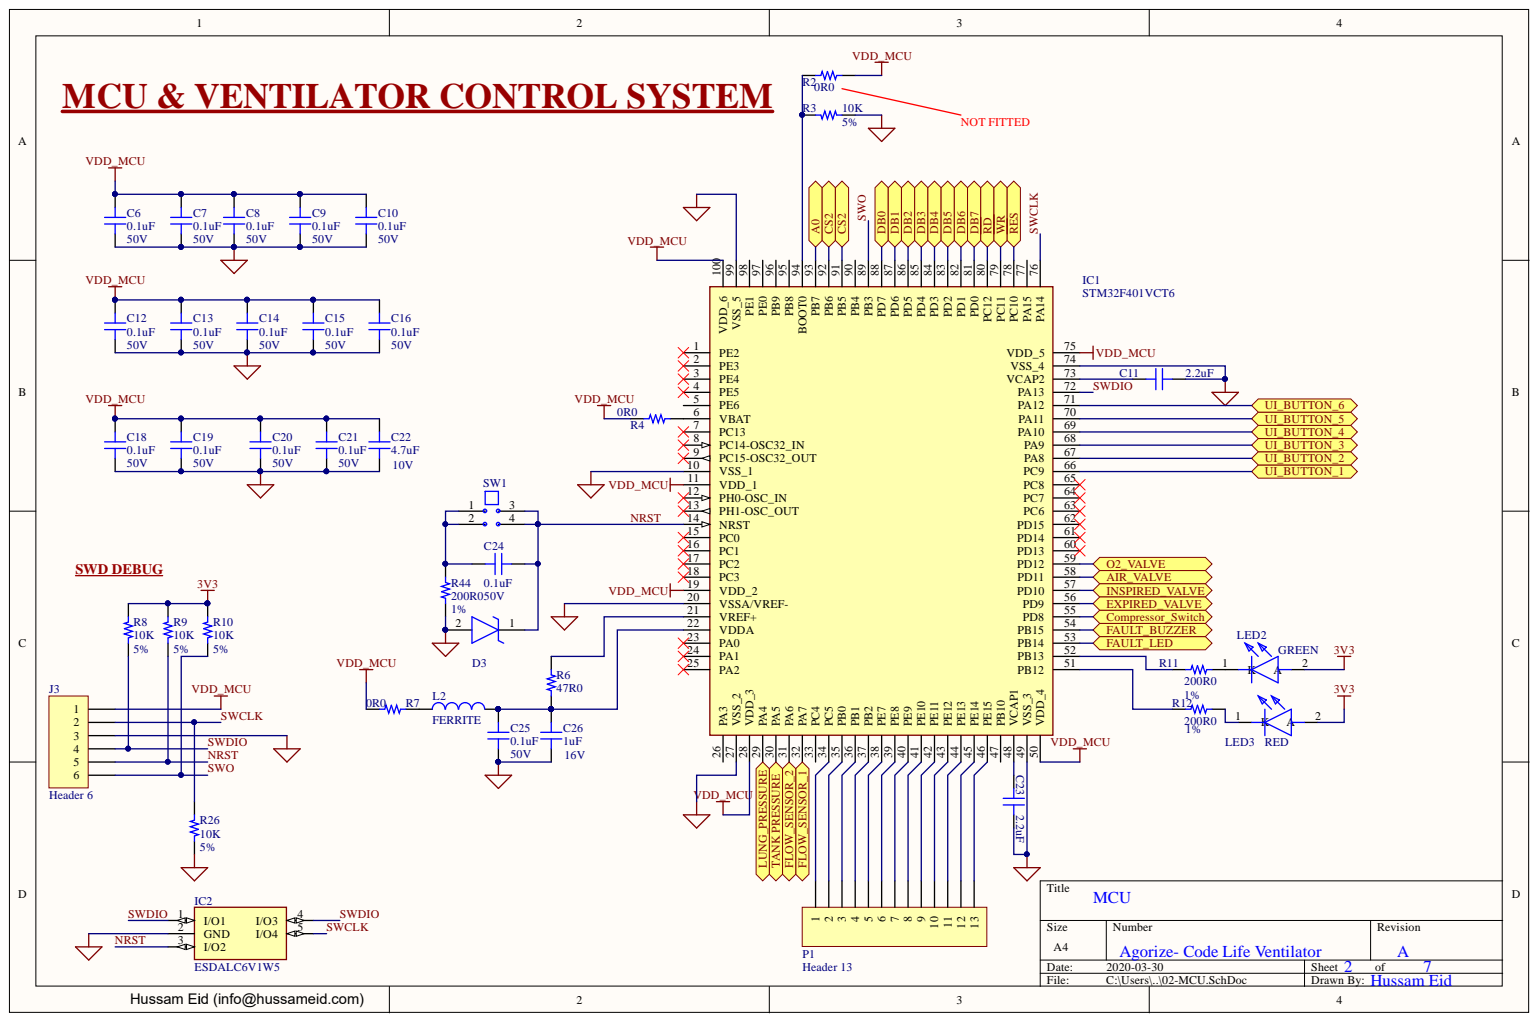
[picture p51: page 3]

MCU & VENTILATOR CONTROL SYSTEM

Agorize- Code Life Ventilator

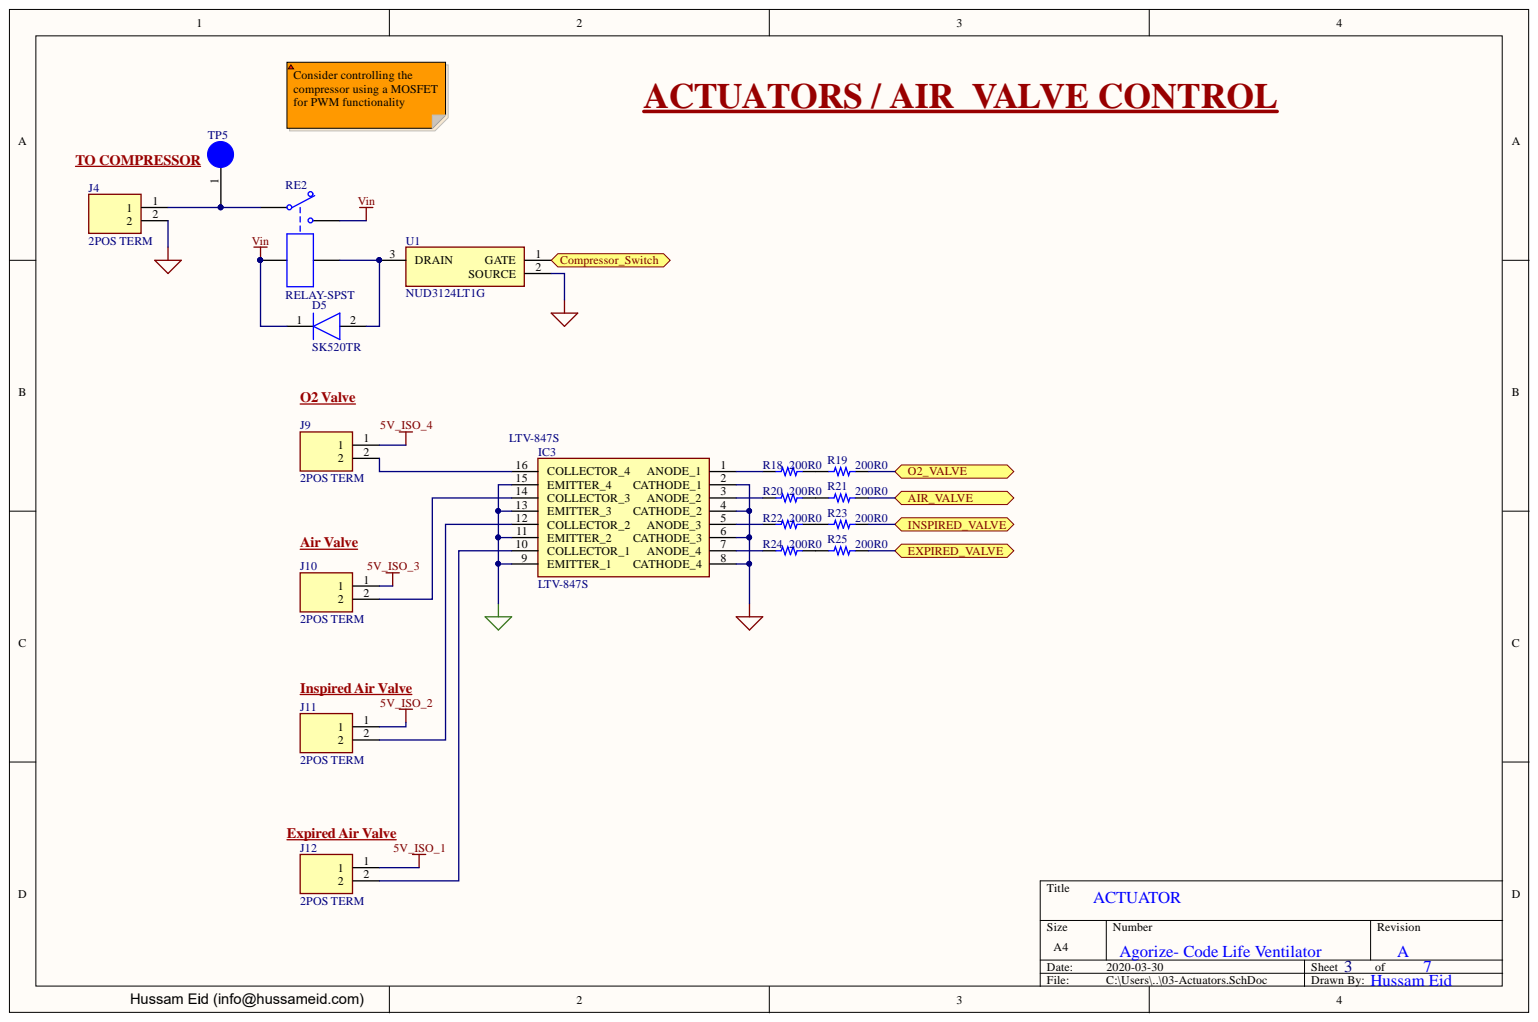
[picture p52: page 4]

ACTUATORS / AIR VALVE CONTROL

EMITTER_4 15

EMITTER_3 13

EMITTER_2 11

EMITTER_1 9

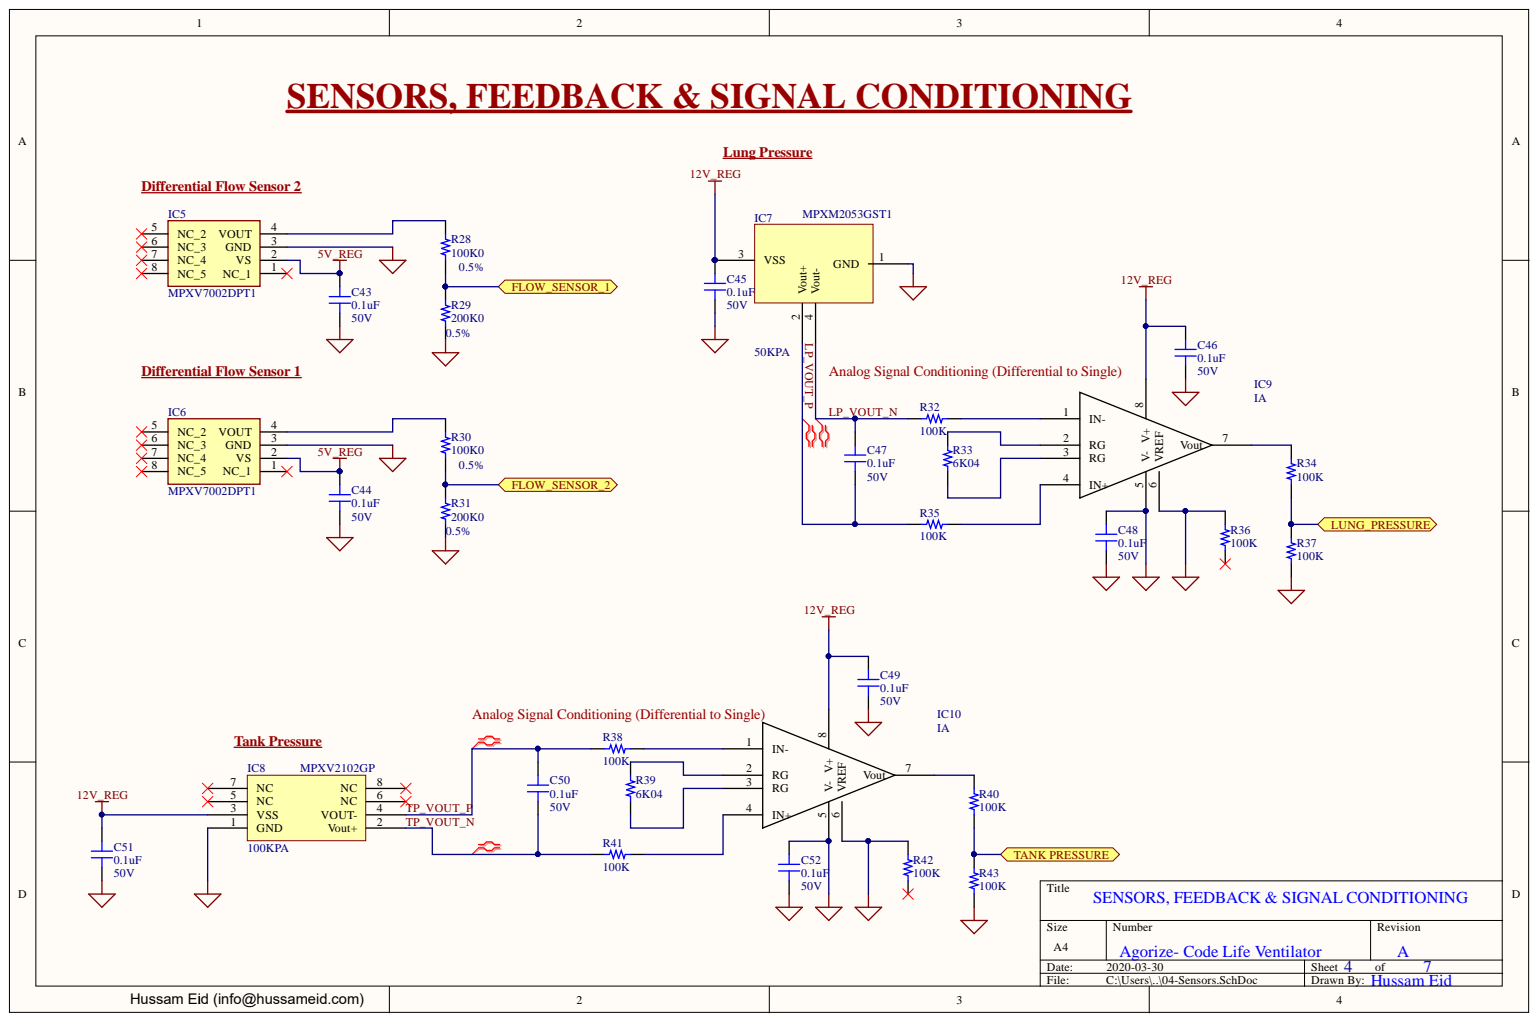
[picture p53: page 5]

SENSORS, FEEDBACK & SIGNAL CONDITIONING

LP_VOUT_P
Analog Signal Conditioning (Differential to Single)

Title

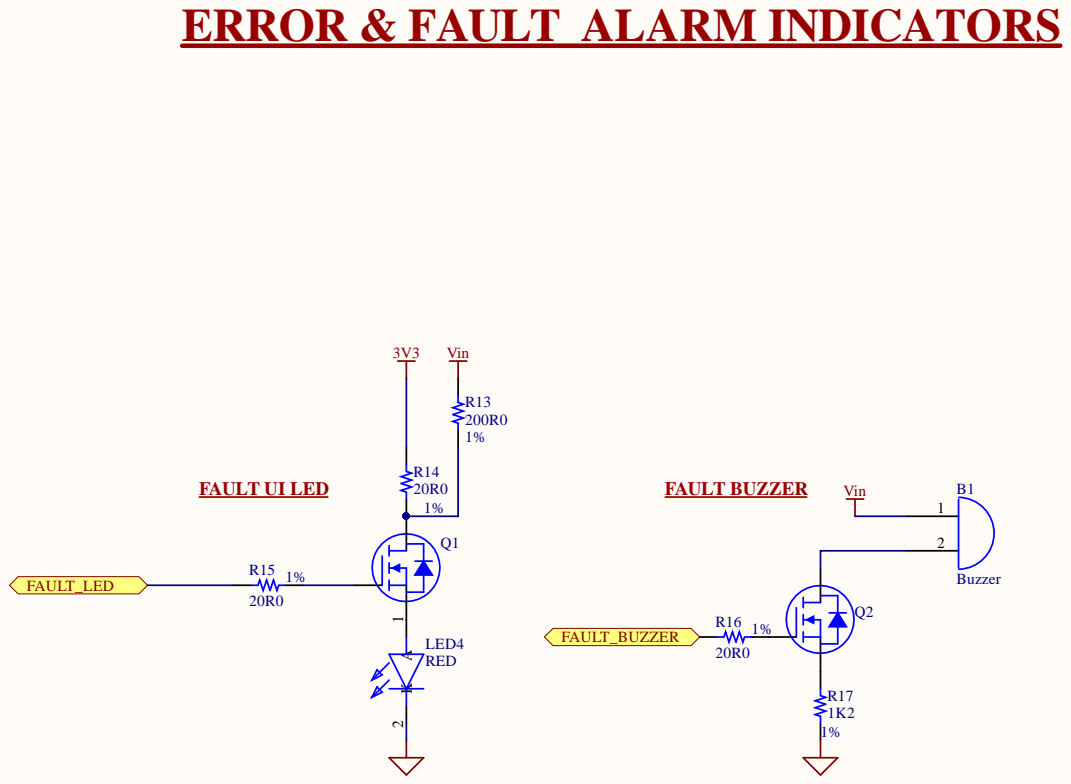
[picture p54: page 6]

ERROR & FAULT ALARM INDICATORS

Title

Agorize- Code Life Ventilator

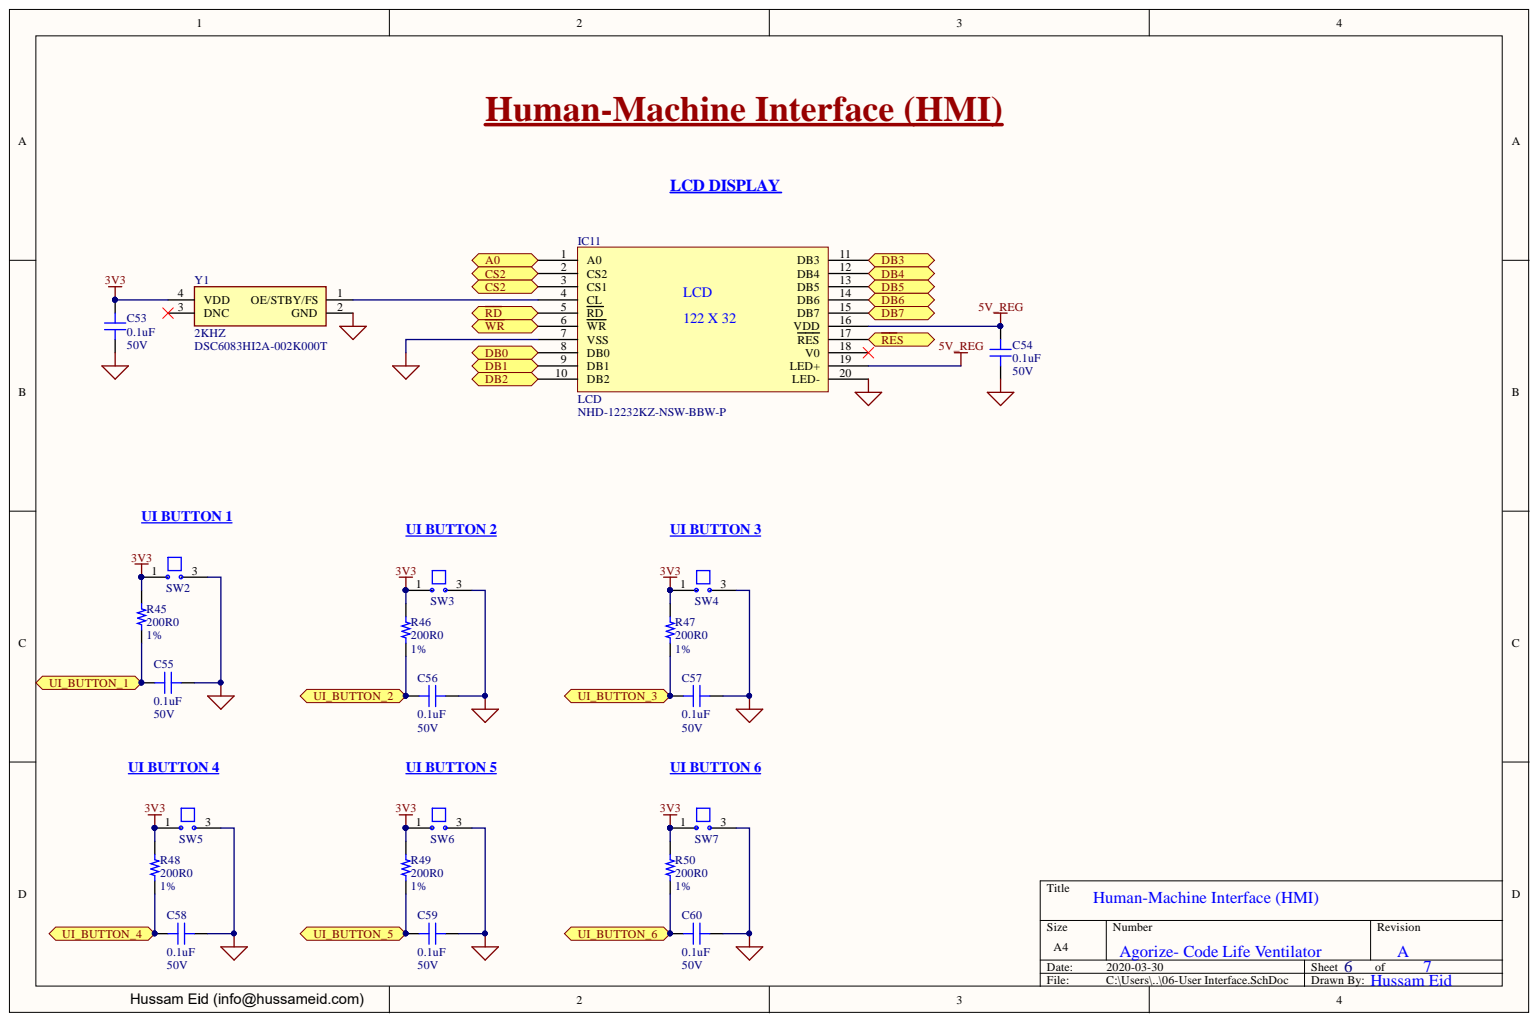
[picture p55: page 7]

Human-Machine Interface (HMI)

Title

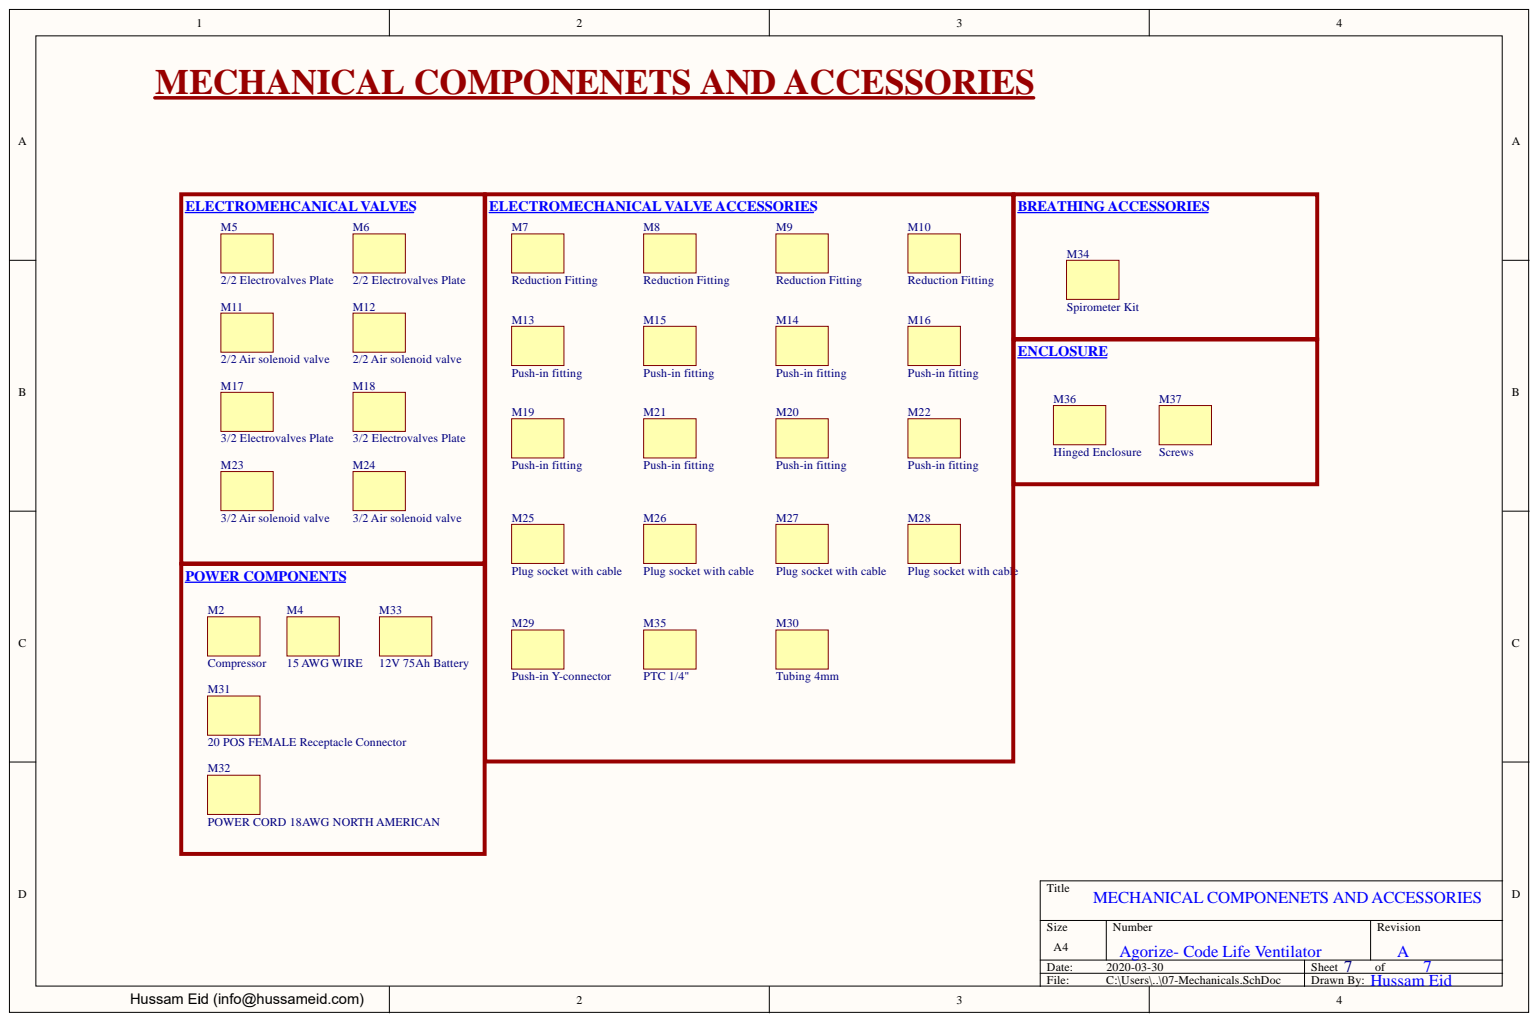
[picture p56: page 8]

MECHANICAL COMPONENETS AND ACCESSORIES

Plug socket with cable

20 POS FEMALE Receptacle Connector

POWER CORD 18AWG NORTH AMERICAN

Title

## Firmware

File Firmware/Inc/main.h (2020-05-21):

/* USER CODE BEGIN Header */
/**
  ******************************************************************************
  * @file           : main.h
  * @brief          : Header for main.c file.
  *                   This file contains the common defines of the application.
  ******************************************************************************
  * @attention
  *
  * <h2><center>&copy; Copyright (c) 2020 STMicroelectronics.
  * All rights reserved.</center></h2>
  *
  * This software component is licensed by ST under BSD 3-Clause license,
  * the "License"; You may not use this file except in compliance with the
  * License. You may obtain a copy of the License at:
  *                        opensource.org/licenses/BSD-3-Clause
  *
  ******************************************************************************
  */
/* USER CODE END Header */

/* Define to prevent recursive inclusion -------------------------------------*/
#ifndef __MAIN_H
#define __MAIN_H

#ifdef __cplusplus
extern "C" {
#endif

/* Includes ------------------------------------------------------------------*/
#include "stm32f4xx_hal.h"

/* Private includes ----------------------------------------------------------*/
/* USER CODE BEGIN Includes */

/* USER CODE END Includes */

/* Exported types ------------------------------------------------------------*/
/* USER CODE BEGIN ET */

/* USER CODE END ET */

/* Exported constants --------------------------------------------------------*/
/* USER CODE BEGIN EC */

/* USER CODE END EC */

/* Exported macro ------------------------------------------------------------*/
/* USER CODE BEGIN EM */

/* USER CODE END EM */

/* Exported functions prototypes ---------------------------------------------*/
void Error_Handler(void);

/* USER CODE BEGIN EFP */

/* USER CODE END EFP */

/* Private defines -----------------------------------------------------------*/
#define LUNG_PRESSURE_Pin GPIO_PIN_4
#define LUNG_PRESSURE_GPIO_Port GPIOA
#define TANK_PRESSURE_Pin GPIO_PIN_5
#define TANK_PRESSURE_GPIO_Port GPIOA
#define FLOW_SENSOR_2_Pin GPIO_PIN_6
#define FLOW_SENSOR_2_GPIO_Port GPIOA
#define FLOW_SENSOR_1_Pin GPIO_PIN_7
#define FLOW_SENSOR_1_GPIO_Port GPIOA
#define LED_DIAGNOSTIC_RED_Pin GPIO_PIN_12
#define LED_DIAGNOSTIC_RED_GPIO_Port GPIOB
#define LED_DIAGNOSTIC_GREEN_Pin GPIO_PIN_13
#define LED_DIAGNOSTIC_GREEN_GPIO_Port GPIOB
#define FAULT_LED_Pin GPIO_PIN_14
#define FAULT_LED_GPIO_Port GPIOB
#define FAULT_BUZZER_Pin GPIO_PIN_15
#define FAULT_BUZZER_GPIO_Port GPIOB
#define COMPRESSOR_SWITCH_Pin GPIO_PIN_8
#define COMPRESSOR_SWITCH_GPIO_Port GPIOD
#define EXPIRED_VALVE_Pin GPIO_PIN_9
#define EXPIRED_VALVE_GPIO_Port GPIOD
#define INSPIRED_VALVE_Pin GPIO_PIN_10
#define INSPIRED_VALVE_GPIO_Port GPIOD
#define AIR_VALVE_Pin GPIO_PIN_11
#define AIR_VALVE_GPIO_Port GPIOD
#define O2_VALVE_Pin GPIO_PIN_12
#define O2_VALVE_GPIO_Port GPIOD
#define UI_BUTTON1_Pin GPIO_PIN_9
#define UI_BUTTON1_GPIO_Port GPIOC
#define UI_BUTTON_2_Pin GPIO_PIN_8
#define UI_BUTTON_2_GPIO_Port GPIOA
#define UI_BUTTON_3_Pin GPIO_PIN_9
#define UI_BUTTON_3_GPIO_Port GPIOA
#define UI_BUTTON_4_Pin GPIO_PIN_10
#define UI_BUTTON_4_GPIO_Port GPIOA
#define UI_BUTTON_5_Pin GPIO_PIN_11
#define UI_BUTTON_5_GPIO_Port GPIOA
#define UI_BUTTON_6_Pin GPIO_PIN_12
#define UI_BUTTON_6_GPIO_Port GPIOA
#define LCD_RES_Pin GPIO_PIN_10
#define LCD_RES_GPIO_Port GPIOC
#define LCD_WR_Pin GPIO_PIN_11
#define LCD_WR_GPIO_Port GPIOC
#define LCD_RD_Pin GPIO_PIN_12
#define LCD_RD_GPIO_Port GPIOC
#define LCD_DB7_Pin GPIO_PIN_0
#define LCD_DB7_GPIO_Port GPIOD
#define LCD_DB6_Pin GPIO_PIN_1
#define LCD_DB6_GPIO_Port GPIOD
#define LCD_DB5_Pin GPIO_PIN_2
#define LCD_DB5_GPIO_Port GPIOD
#define LCD_DB4_Pin GPIO_PIN_3
#define LCD_DB4_GPIO_Port GPIOD
#define LCD_DB3_Pin GPIO_PIN_4
#define LCD_DB3_GPIO_Port GPIOD
#define LCD_DB2_Pin GPIO_PIN_5
#define LCD_DB2_GPIO_Port GPIOD
#define LCD_DB1_Pin GPIO_PIN_6
#define LCD_DB1_GPIO_Port GPIOD
#define LCD_DB0_Pin GPIO_PIN_7
#define LCD_DB0_GPIO_Port GPIOD
#define LCS2CD__Pin GPIO_PIN_5
#define LCS2CD__GPIO_Port GPIOB
#define LCD_CS2_Pin GPIO_PIN_6
#define LCD_CS2_GPIO_Port GPIOB
#define LCD_A0_Pin GPIO_PIN_7
#define LCD_A0_GPIO_Port GPIOB
/* USER CODE BEGIN Private defines */

/* USER CODE END Private defines */

#ifdef __cplusplus
}
#endif

#endif /* __MAIN_H */

/************************ (C) COPYRIGHT STMicroelectronics *****END OF FILE****/
